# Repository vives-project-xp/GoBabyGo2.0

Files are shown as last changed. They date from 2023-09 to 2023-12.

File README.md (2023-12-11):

# GoBabyGo2.0

# Inhoudsopgave
1. [Inleiding](#inleiding)
2. [Nodige Onderdelen](#nodige-onderdelen)
3. [BOMlijst](#bomlijst)
4. [Rand Info](#rand-info)
5. [Digitale Joystick](#digitale-joystick)
6. [Analoge Joystick](#analoge-joystick)
7. [Motor Driver](#motor-driver)
8. [Potentiometer](#potentiometer)
9. [DC-DC Buck Converter](#dc-dc-buck-converter)
10. [Montage Ideeën](#montage-ideeën)
11. [PCB](#PCB)
12. [ESP32 Pinout](#esp32-pinout)

Alle info over het installeren van nodige programma's om te kunnen programmeren staat in het mapje [Programma's](./Programma's)

## inleiding
Ons doel is om kinderen met beperkte mobiliteit meer bewegingsvrijheid te geven. We vervangen het traditionele pedaal in auto's door een joystick die via een afstandsbediening kan worden bediend. De afstandsbediening heeft voorrang op de joystick. We hebben twee concepten voor de bevestiging van de joystick aan de auto: een dashboardmontage die de joystick van links naar rechts verplaatst, en een zijkantmontage die aan beide kanten kan worden geplaatst. Het brein van de auto is een ESP die de joystickinvoer leest en de motoren aanstuurt. Omdat de positie van de voorwielen niet kan worden ingelezen met de bestaande auto hardware, gebruiken we een potentiometer om dit probleem op te lossen.

## Nodige onderdelen

- Auto
- MicroController
- Motor driver voor te kunnen sturen
- Joystick
- DC-DC Converter

## BOMlijst
| **Onderdeel**            | **Prijs** | **Link**                                                                                                                                                                                                                                                                |
|--------------------------|-----------|-------------------------------------------------------------------------------------------------------------------------------------------------------------------------------------------------------------------------------------------------------------------------|
| **Motor Driver**         | €5.29     | https://www.amazon.com.be/-/en/OcioDual-Stepper-Electronics-Projects-Raspberry/dp/B07YNR5KWP/ref=sr_1_10?crid=13WDD3RB1V2TC&keywords=l298n+motor+driver&qid=1695624708&sprefix=l298n+motor+driver%2Caps%2C69&sr=8-10                                                    |
| **ESP32**                | €11.37    | https://www.amazon.com.be/-/en/ESP-32S-Development-Antenna-Bluetooth-Arduino/dp/B07XH45MWW/ref=sr_1_27?crid=2R7CSQ30VFE6H&keywords=esp32&qid=1695629494&sprefix=esp32%2Caps%2C166&sr=8-27&th=1                                                                          |
| **Joystick**             | €14.21    | https://www.amazon.com.be/-/en/Potentiometer-JH-D202X-R2-Controller-Photography-Accessories/dp/B09J2C4DN5/ref=sr_1_3?crid=357R56FNH75R6&keywords=Joystick+potentiometer+JH-D202X-R4+10K&qid=1695624613&sprefix=joystick+potentiometer+jh-d202x-r4+10k%2Caps%2C66&sr=8-3 |
| **DC-DC Buck Converter** | €11.88    | https://www.amazon.com.be/-/en/Hailege-Converter-1-25-36V-Adjustable-Step-down/dp/B07XRF9NWP/ref=sr_1_7?crid=1PQTSHA11MF1Q&keywords=dc+to+dc+buck+converter+adjustable&qid=1695628749&sprefix=dc+to+dc+buck+converter+adjustable%2Caps%2C71&sr=8-7                      |
| **Optocoupler** | €7.85    | https://www.amazon.com.be/-/en/BOJACK-Optocoupler-Installation-Spacing-Package/dp/B08CXKZ98W/ref=sr_1_6?crid=1FXUJNO9624LN&keywords=optocoupler&qid=1695634939&sprefix=optocoupler%2Caps%2C69&sr=8-6                      |
| **Connector PCB-Kabels** | €10.24    | https://www.amazon.com.be/-/en/Litorange-Female-2-54mm-JST-XH-Connector/dp/B086W9HB3M/ref=sr_1_1?crid=SXDRC5SCF07L&keywords=Picture+1+of+24+Click+to+enlarge+Have+one+to+sell%3F+Sell+it+yourself+Terminal+Board+Connectors+JST+Male+Female&qid=1695648512&s=home-improvement&sprefix=picture+1+of+24+click+to+enlarge+have+one+to+sell+sell+it+yourself+terminal+board+connectors+jst+male+female%2Chome-improvement%2C199&sr=1-1                      |
| **Connector kabels-kabels** | €13.99    | https://www.amazon.com.be/-/en/HSeaMall-Connector-Female-Housing-Assortment/dp/B0716WZ6RW/ref=sr_1_12?crid=3B4MFSYF52HO6&keywords=JST+conector+set&qid=1696247641&s=home-improvement&sprefix=jst+conector+set%2Chome-improvement%2C66&sr=1-12                     |
| **potentiometer** | €9.11    | https://www.amazon.com.be/-/en/Potentiometer-Rotating-Automotive-Electronics-Multimedia/dp/B09BJMFVMZ/ref=sr_1_11?crid=3GKNUFMRX9EJO&keywords=potentiometer+10k&qid=1696248212&s=home-improvement&sprefix=potentiometer+10k%2Chome-improvement%2C259&sr=1-11                      |

## Rand info

Batterij is 12v 

De huidige electronica komen de kabels met het volgende overeen:

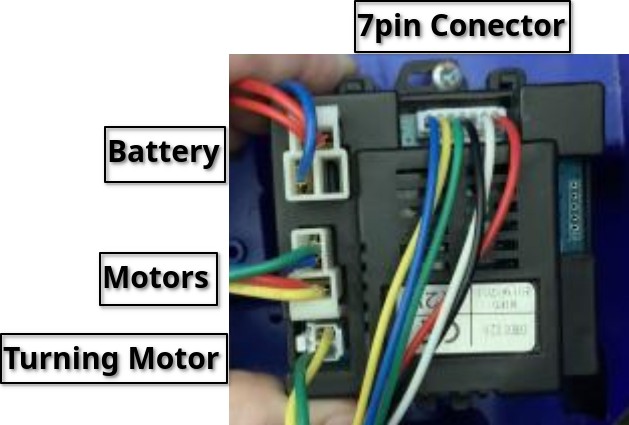
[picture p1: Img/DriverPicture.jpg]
Driver


De 7Pin Connector:
- Blauw: low high speed
- geel: vooruit
- Groen: achteruit
- zwart: grond
- empty
- wit: aanuitknop
- rood: aanuitknop

## Digitale Joystick
Om de auto te besturen zullen we een joystick gebruiken. De joystick die we in het begin tot onze beschikking hebben, is digitaal. 
In de toekomst overwegen we mogelijk over te schakelen naar een analoge joystick. Hoe je de joystick kunt binnenlezen kun je vinden onder het mapje [Programma's](./Programma's).

Zorg er voor dat de connector links onder zit dan klopt het schema.

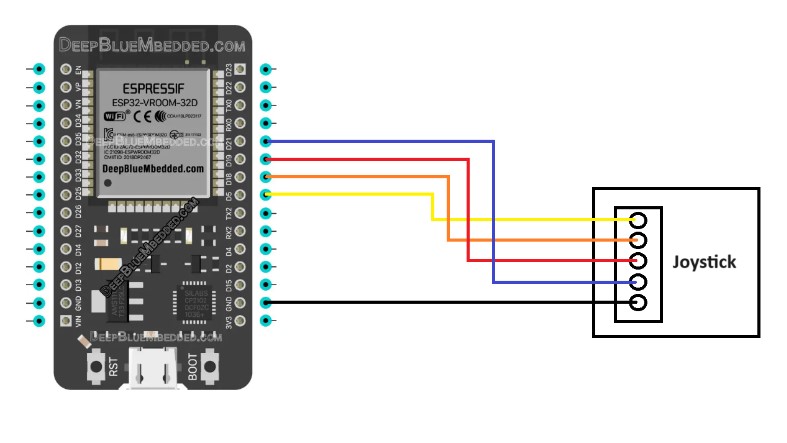
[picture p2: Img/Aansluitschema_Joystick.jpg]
Aansluitschema Joystick


## Analoge Joystick
Na het gebruik van een digitale joystick stappen we nu over naar een analoge variant voor het besturen van de auto. Een analoge
joystick maakt gebruik van variabele weerstand, waardoor we een vloeiendere en nauwkeurigere stuurinvoer kunnen realiseren. Ons
eindprogramma zal dan ook ontwikkeld worden met een analoge joystick. We hebben echter geen tussen programma's voor de analoge
joystick, omdat we deze al hebben gemaakt voor de digitale variant. Het zou overbodig zijn om dit proces opnieuw uit te voeren voor
de analoge joystick.

Een analoge joystick heeft twee potmeters. De beweging van de joystick zorgt voor variabele weerstand. Elke potmeter vertegenwoordigt
een richting: vooruit en achteruit (y-as) en links en rechts (x-as). Deze weerstanden worden omgezet in elektrische signalen, die
vervolgens worden gebruikt om de auto aan te sturen.

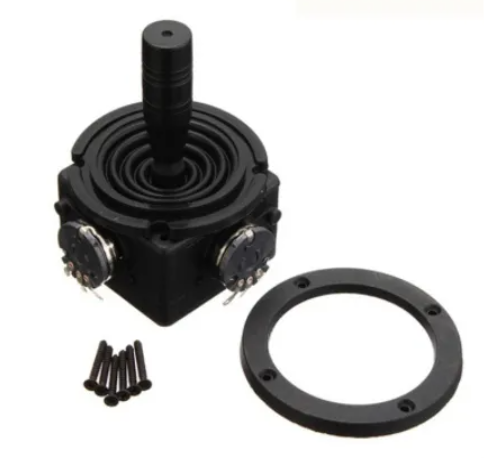
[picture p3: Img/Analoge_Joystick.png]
Analoge Joystick


## Motor driver
Om de richting te bepalen van de auto gebruiken we een motortje. Dit motortje wordt aangestuurd a.d.h.v een driver. 
Via deze driver kunnen we de richting en de snelheid van de motor bepalen. De driver die wij gebruiken is de L298N.
Hoe je de driver kunt gebruiken met een ESP kun je vinden in het mapje [Programma's](./Programma's).

De L298N is een motorcontroller-IC dat vaak wordt gebruikt in elektronische projecten. Het maakt gebruik van een H-brug-configuratie, waardoor het mogelijk is om
gelijkstroommotoren in beide richtingen aan te sturen. Met twee onafhankelijke kanalen is het geschikt voor het afzonderlijk aansturen van twee motoren, zoals bij
robotica wij gebruiker hier maar 1 van. Het ondersteunt een breed spanningsbereik en wordt gecontroleerd met logische signalen van bijvoorbeeld een microcontroller
zoals Arduino.

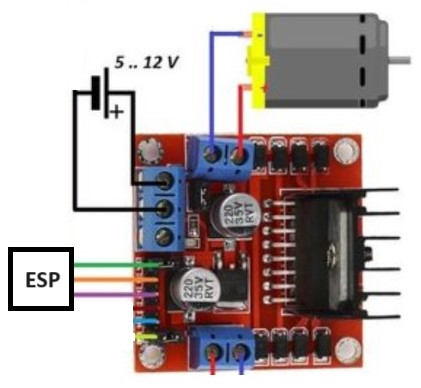
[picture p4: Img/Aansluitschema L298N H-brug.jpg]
Aansluitschema Driver
 

- Oranje,Paars: Richting motor
- Groen: Snelheid motor

## Potentiometer
Om de positie van onze wielen vast te stellen, maken we gebruik van een potentiometer. Een potentiometer, kortweg pot meter, is een elektronisch component dat wordt
ingezet om een variabele weerstand te creëren in een elektrisch circuit. In ons geval genereren we een analoog signaal op basis van deze weerstandswaarden, waarmee we
de positie van het stuur kunnen bepalen. Concreet wordt de potentiometer aan de stang bevestigd, die op zijn beurt is gekoppeld aan de wielen van de auto. Wanneer de
wielen van positie veranderen, wijzigt ook de positie van de potentiometer, waardoor we nauwkeurig de positie van de wielen kunnen achterhalen.

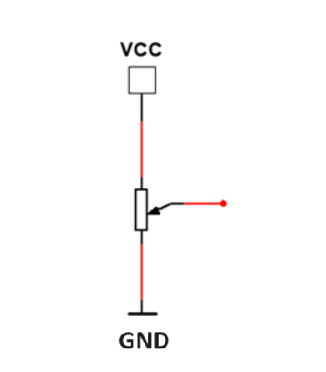
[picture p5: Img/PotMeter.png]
PotMeter


## DC-DC Buck Converter
Omdat niet al onze componenten op dezelfde spanning werken gebruiken we een Buck converter. Deze zorgt er voor dat we een hogere spanning
kunnen omzetten naar een lagere spanning. In de auto hebben we een baterij ter beschikking van 12 Volt maar onze esp heeft maar 5 volt nodig. 

Een DC-DC buck converter is een elektronisch apparaat dat de ingangsspanning van een gelijkstroombron verlaagt naar een lagere uitgangsspanning. Het werkt als een
efficiënte schakelende regelaar met behulp van componenten zoals transistors en een spoel (inductor). Deze converters worden veel gebruikt in elektronische apparaten om
de benodigde lagere spanning te leveren, zoals in batterijgevoede apparaten en voedingen voor microcontrollers.

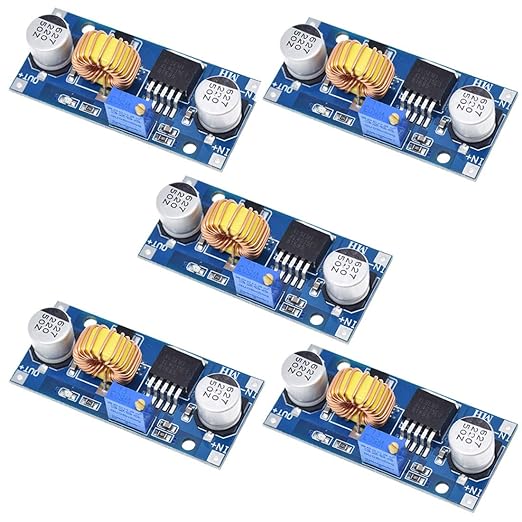
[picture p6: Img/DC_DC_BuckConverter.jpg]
BuckConverter


## montage ideeën
De joystick mag niet te veel ruimte innemen in de auto. Deze is geplaatst in een 3D-geprinte behuizing die aan een PVC-buis is bevestigd. We hebben voor een PVC-buis gekozen vanwege het lichte gewicht en de
mogelijkheid om de bekabeling erin te verbergen. We hebben twee concepten ontwikkeld voor het monteren van de joystick in de auto. Bij het eerste concept is de buis bevestigd aan het dashboard. Voor het tweede
concept wordt de buis aan de deur gemonteerd. In beide concepten kan de joystick links of rechts worden geplaatst, afhankelijk van de mobiliteit van het kind. We bevestigen de buizen met clips aan de auto.

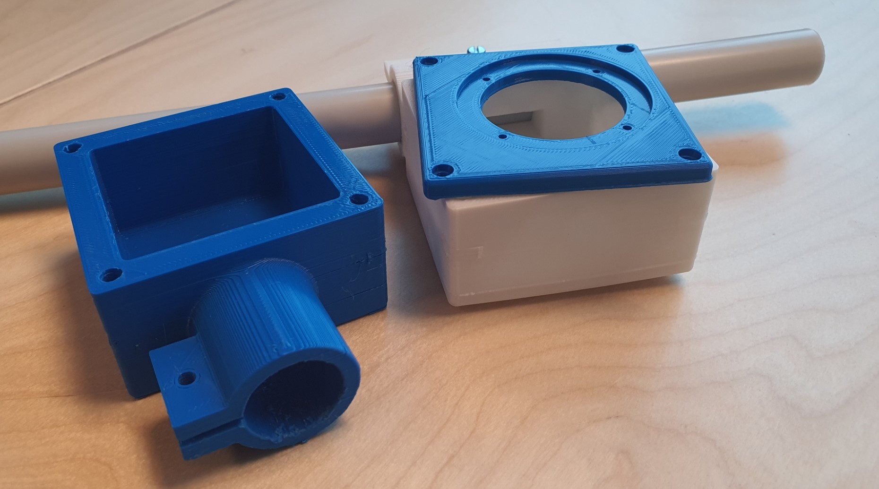
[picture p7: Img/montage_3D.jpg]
joystickbox


## PCB

### Inleiding

Meer info staat in de PCB directory.

### PCB layout

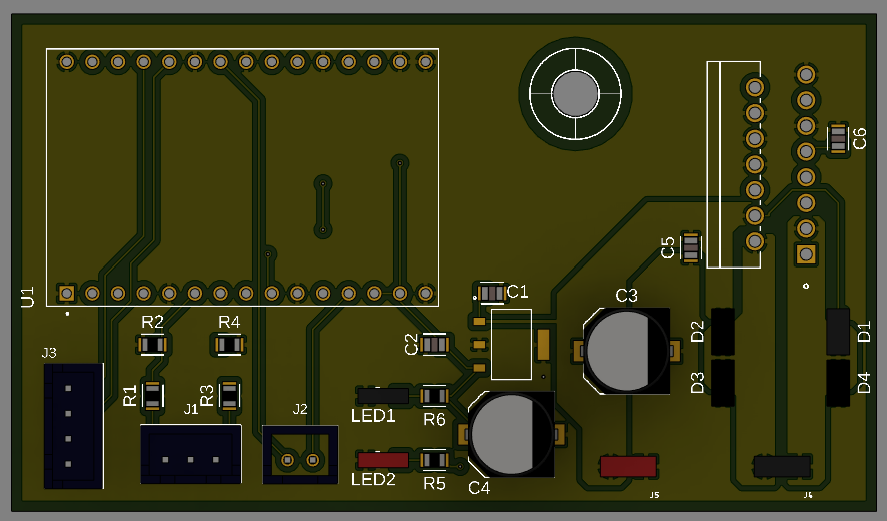
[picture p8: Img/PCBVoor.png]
PCBVoor


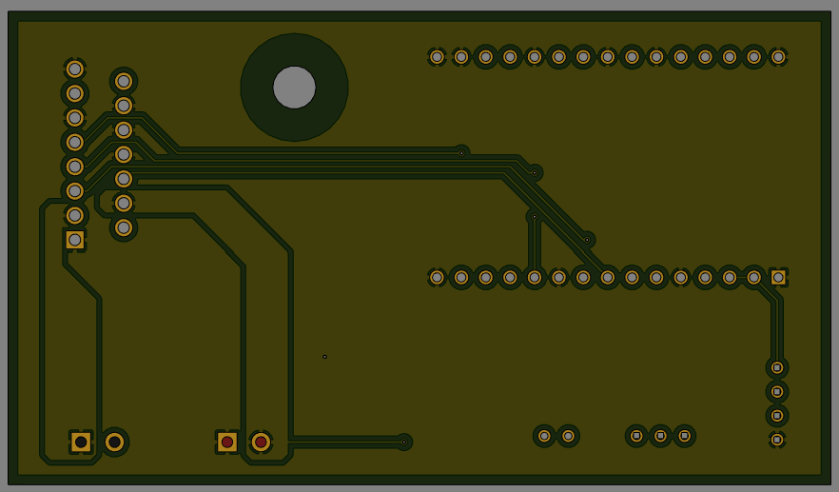
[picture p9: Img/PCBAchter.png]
PCBAchter


## ESP32 Pinout
- Driver
  - In1 = GPIO23
  - In2 = GPIO22
  - ENA = GPIO21
  - Channel = GPIO13

- Huidige elektronica
  - Forward = GPIO15
  - Backward = GPIO19
- Joystick
  - Xpin = GPIO2
  - Ypin = GPIO4

- Potentiometer
  - potPin = GPIO14

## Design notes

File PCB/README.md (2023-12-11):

# PCB

## inleiding

Ideal zouden we een PCB kunnen maken. Hier een korte aanzet om er aan te starten.

## Project files

De files zijn de archive en de .lbr.

## componenten

### Connectoren

Wel we hebben connectoren nodig.

- Connectoren set: https://www.amazon.com.be/-/en/YIXISI-Pieces-Connector-Connectors-Terminals/dp/B082ZLYRRN/ref=sr_1_1?crid=1NRPVG0VJ7JD6&keywords=Litorange%2B500%2Bx%2BJST%2BMale%2Band%2BFemale%2B2.54mm%2BJST-XH%2BJST%2BConnector%2Bwith%2BFemale%2BPin%2BConnector%2BWhite&qid=1701683827&s=home-improvement&sprefix=litorange%2B500%2Bx%2Bjst%2Bmale%2Band%2Bfemale%2B2.54mm%2Bjst-xh%2Bjst%2Bconnector%2Bwith%2Bfemale%2Bpin%2Bconnector%2Bwhite%2B%2Chome-improvement%2C73&sr=1-1&th=1
- Screw Terminals: https://be.farnell.com/multicomp-pro/mp011984/tb-wire-to-brd-r-a-2way-18awg/dp/4179014?st=screw%20terminals

### Gekozen componenten

De gebruikte componenten:
 - L298N : https://be.farnell.com/stmicroelectronics/l298n/ic-bridge-driver-dual-298/dp/403295?ICID=I-RP-STM7REC-1
 - ESP32 (->devkit<-) : https://www.mouser.be/ProductDetail/Espressif-Systems/ESP32-C3-DevKitC-02?qs=stqOd1AaK7%2F1Q62ysr4CMA%3D%3D
 - Voltage regulators : 
    -  5V: https://be.farnell.com/diodes-inc/az1117ch2-5-0trg1/ldo-dc-dc-conv-5v-0-8a-sot-223/dp/3942512
 - Diode: https://be.fa rnell.com/taiwan-semiconductor/es1dl-r3g/diode-ultra-fast-smf-1a-200v/dp/1559127
 - LEDs:
    - Green: https://be.farnell.com/multicomp-pro/mp008255/led-green-80mcd-576nm-1206/dp/3796283
    - Red: https://be.farnell.com/multicomp-pro/mp008281/led-red-100mcd-638nm-1206/dp/3796312
 - Weerstanden en condesatoren: Zie bomlijst.

 ### Reden keuze

Zie architectuur documenten om te zien wat we willen berijken. </br>

- L298N: Het is een veel gebruikte motordriver en simple te gebruiken.
- ESP32 Devkit: Dit hebben we liggen en het is dan gemakelijker om een pcb te maken. Moet geen rekening houden met de USB -> UART interface en we hebben dan geen 3.3V LDO meer nodig dan.
- Voltage regulator: we hebben 5V nodig voor de ESP en de MotorDriver te logica te voeden.

## Elektrisch schema

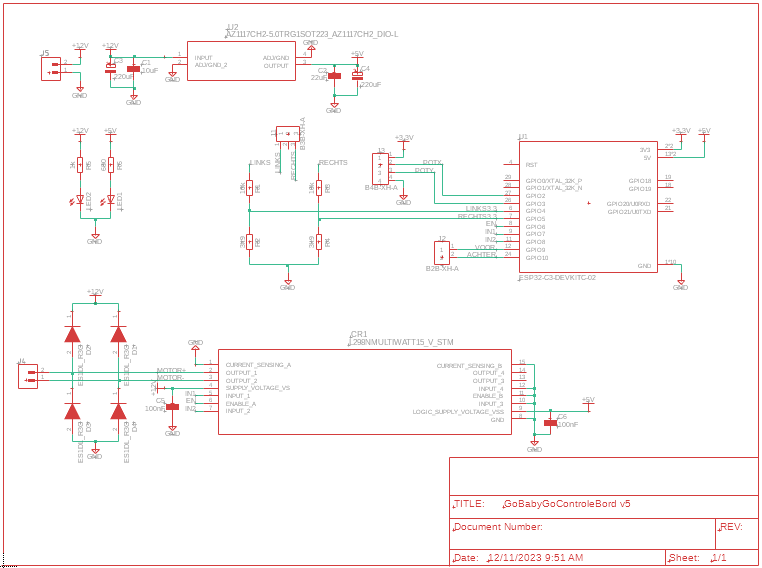
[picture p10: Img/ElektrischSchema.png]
Elektrisch schema


## PCB layout

PCBVoor

PCBAchter

## Bekabeling

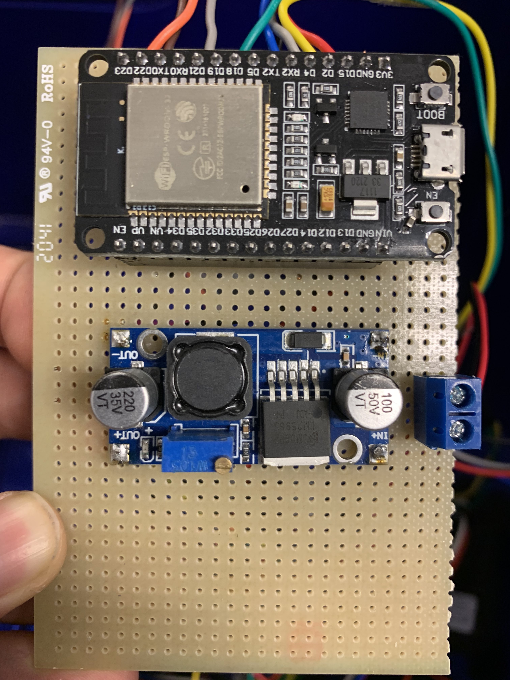
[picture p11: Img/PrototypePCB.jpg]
PrototypePCB


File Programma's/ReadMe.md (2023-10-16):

# Programma's

Om onze auto te laten rijden met behulp van een joystick, moeten we programmeren. Er zijn verschillende programma's om de verschillende delen van het project te testen. Deze programma's vormen allemaal bouwstenen die uiteindelijk het eindprogramma vormen.

## Voorbereiding 

Om te kunnen programmeren moeten we eerst verschillende programma's downloaden. Welke programma's je moet downloaden en hoe het werkt, kun je hieronder vinden.

### Arduino

Als je de verschillende tussenprogramma's wilt testen zul je arduino moeten downloaden. Dit kun je makkelijk downloaden via volgende
[Link](https://support.arduino.cc/hc/en-us/articles/360019833020-Download-and-install-Arduino-IDE "Arduino downloaden"). Arduino is een open-source elektronisch platform dat programmeerbaar is en gemakkelijk te gebruiken, zelfs voor beginners.

### Visual Studio Code

Ons eindprogramma wordt ontwikkeld in Visual Studio Code, een krachtige en veelzijdige code-editor die populair is vanwege zijn gebruiksvriendelijke interface en uitbreidbare functionaliteiten. Om deze code naar de ESP32 te uploaden, maken we gebruik van PlatformIO, een handige extensie voor Visual Studio Code die specifiek is ontworpen voor het bouwen en uploaden van code naar verschillende microcontrollerplatforms. Visual Studio Code is eenvoudig te downloaden en te gebruiken, en je kunt de nieuwste versie verkrijgen vanaf de officiële [website](https://code.visualstudio.com/download).

In Visual Studio Code moeten we nu PlatformIO downloaden. Als je links op "Extensions" klikt symbool met de vierkantjes, kun je zoeken naar PlatformIO en het vervolgens installeren.

| Opzoeken PlarformIO | PlarformIO installeren |
|--------------|--------------|
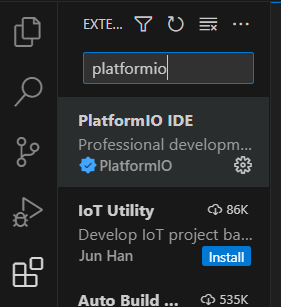
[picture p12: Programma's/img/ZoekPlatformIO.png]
Opzoeken PlarformIO
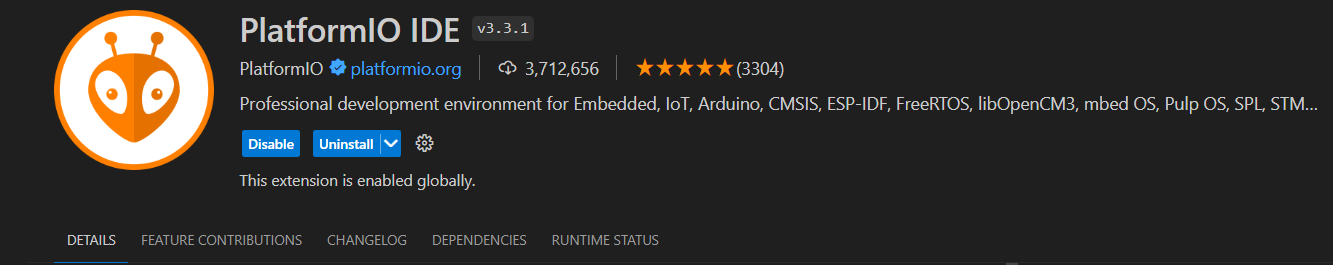
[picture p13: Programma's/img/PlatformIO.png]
PlarformIO installeren
|  ||

Om het eindprogramma te openen, ga je naar de map 'Eindprogramma' en open je Visual Studio Code via de terminal. Dit doe je door met de rechtermuisknop te klikken in de map 'Eindprogramma' en te kiezen voor 'Openen in terminal'. Zodra je in de terminal bent, typ je "code ." en druk je op Enter. Nu kun je het programma in Visual Studio Code uploaden naar je ESP32. De code zelf vind je in de 'src' map.

| Terminal openen | visual studio code openen |
|--------------|--------------|
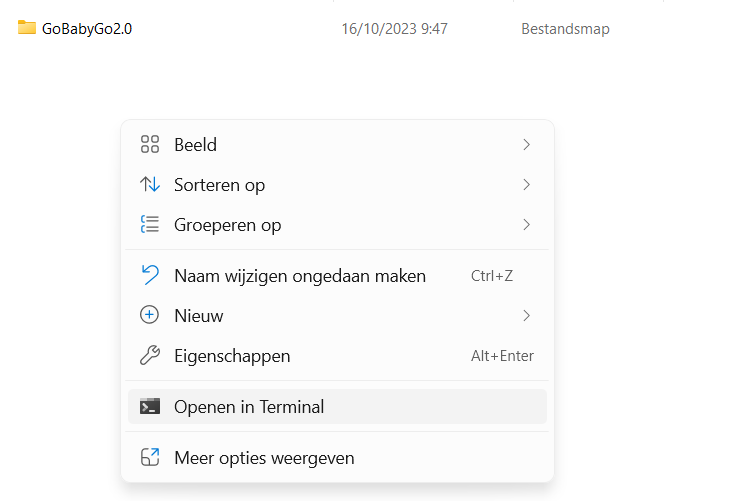
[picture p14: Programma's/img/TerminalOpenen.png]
Terminal openen
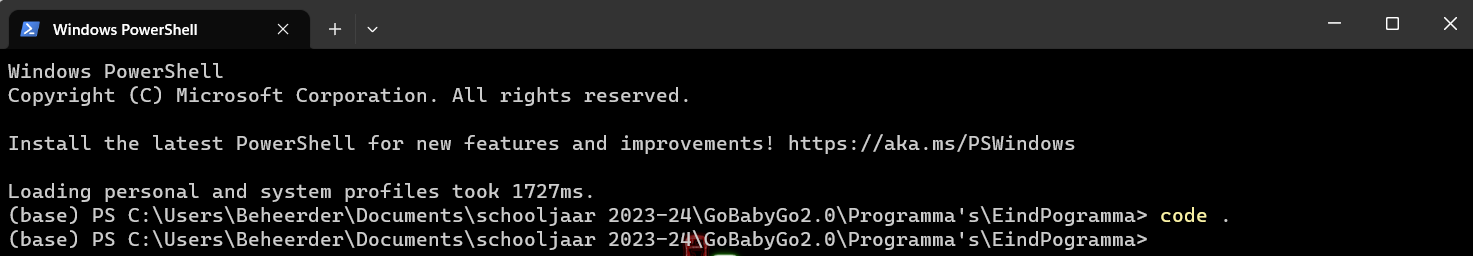
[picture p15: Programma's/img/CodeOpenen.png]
Code openen
|  ||

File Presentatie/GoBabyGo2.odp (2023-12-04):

## GoBabyGo2.0

Axel Brouckaert

Robbe De Wispelaere

Nikita Vandecasteele

## Analyse

- Stuur vervangen
- Joystick
- Bekabeling
- Programmeren
- Besturing ontwerp

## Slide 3

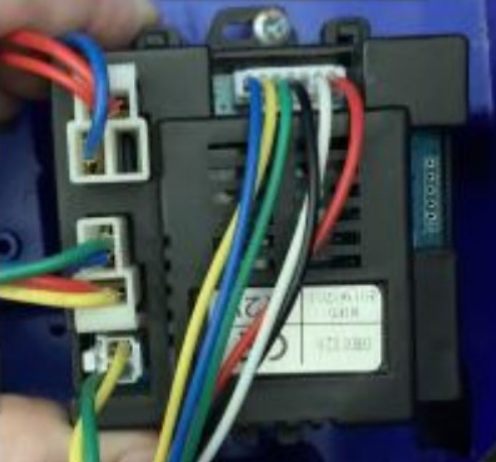
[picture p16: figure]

Onderzoek auto

- Welke elektronica zit er in?
- Bekabeling behouden?
- Eigen inbreng.

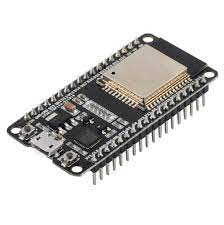
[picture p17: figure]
Amazon.com: DIYmall ESP32 DEVKIT ESP32-WROOM-32 Development Board ESP32 ESP-32S 2.4GHz WiFi+BT BLE Dual-core Dev Module CP2102 for Arduino DOIT : Electronics

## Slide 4

Bestaande besturing

De 7Pin Connector:

- Blauw: low high speed
- Geel: vooruit
- Groen: achteruit
- Zwart: grond
- Empty
- Wit: aanuitknop
- Rood: aanuitknop

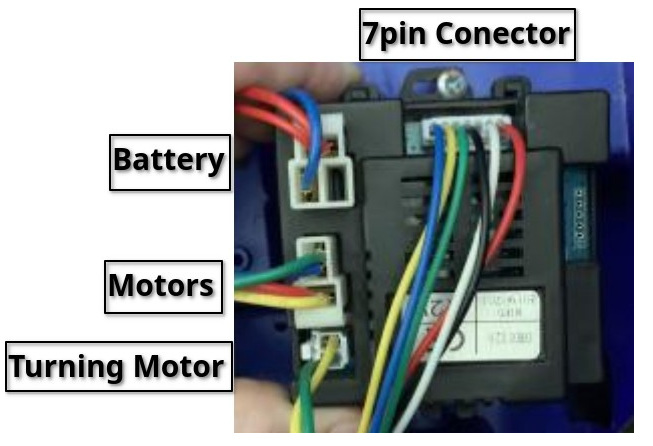
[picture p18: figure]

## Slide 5

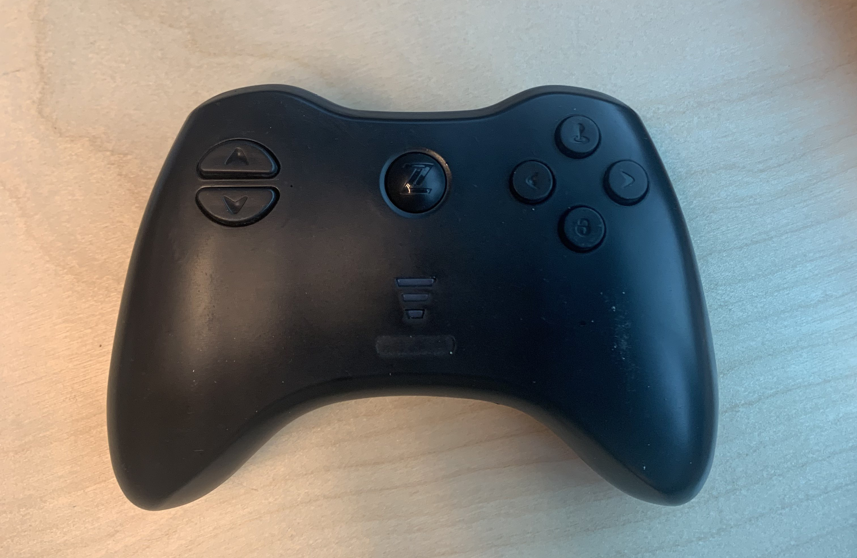
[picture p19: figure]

Nieuwe besturing

- Analoge of digitale Joystick?
- Wat met controller?

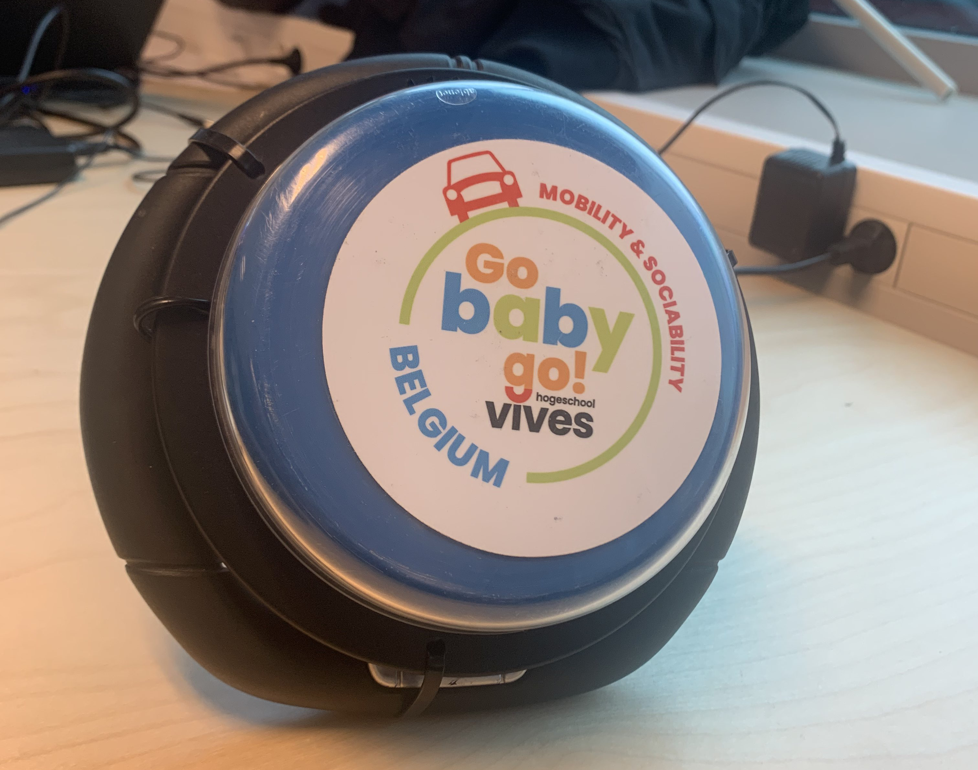
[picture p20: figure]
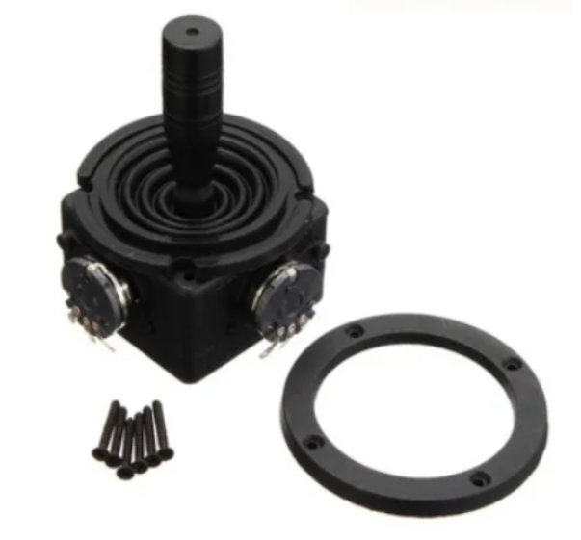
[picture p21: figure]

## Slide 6

Nieuwe Besturing

- Arduino
- Platform IO

Richting

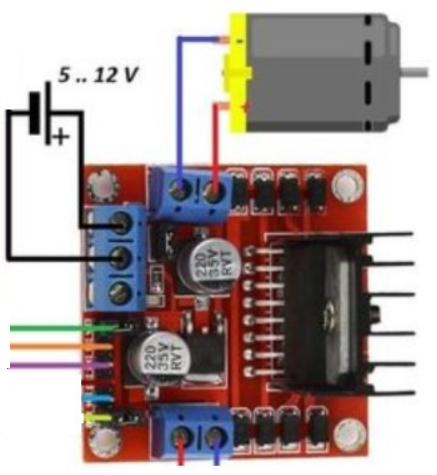
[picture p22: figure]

Snelheid V/A

Positie stuur

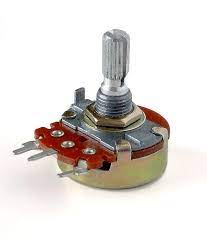
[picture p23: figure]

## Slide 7

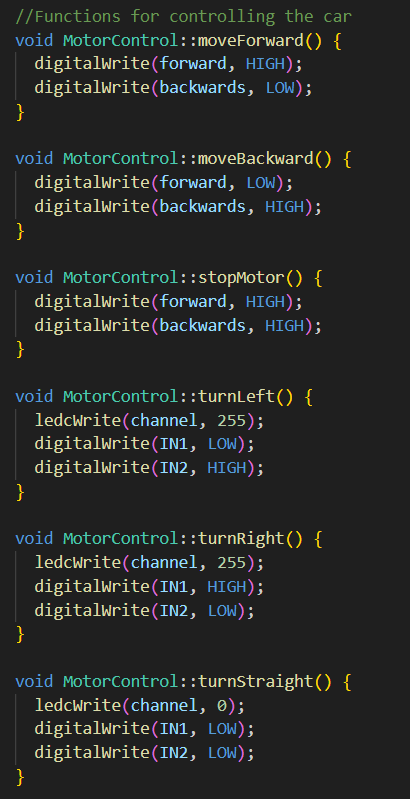
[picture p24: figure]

Praktische uitvoer

- Joystick binnen lezen
- Motor v/a aansturen
- Motor richting aansturen
- Potmeter binnen lezen
- Richting wielen bepalen

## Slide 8

Montage

- 2 concepten
- 3d prints
- Pvc buizen


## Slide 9

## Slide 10

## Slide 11

Niet afgewerkt

- Positie wielen bepalen.
- Automatisch positie van wielen naar midden.

Eindconclusie

Afgewerkt

- Joystick binnen lezen.
- Richting auto.
- Vooruit/Achteruit.
- Bekabeling in auto

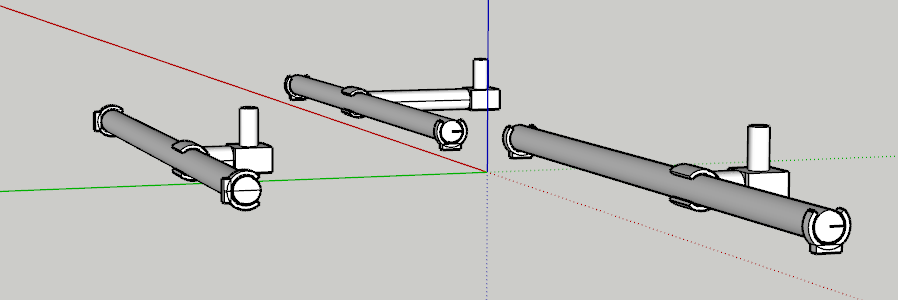
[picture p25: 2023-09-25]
Img/4schets3D.PNG

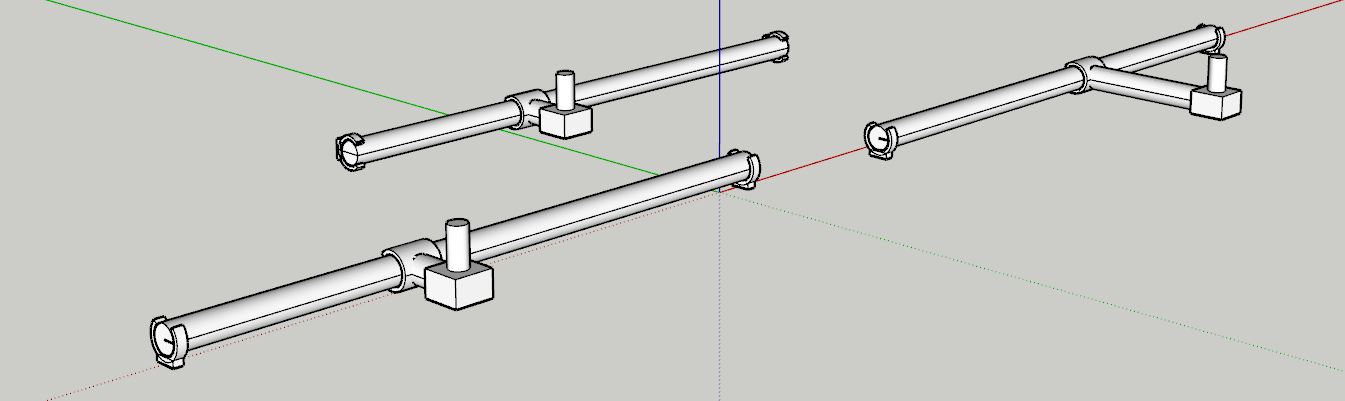
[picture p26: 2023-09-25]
Img/2schets3D.PNG

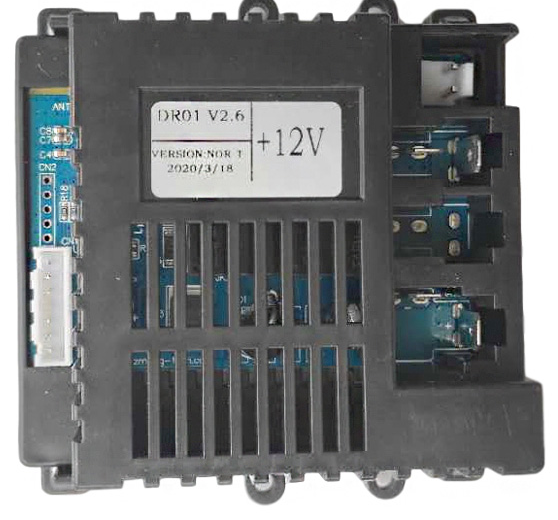
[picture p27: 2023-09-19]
Img/Driver.png

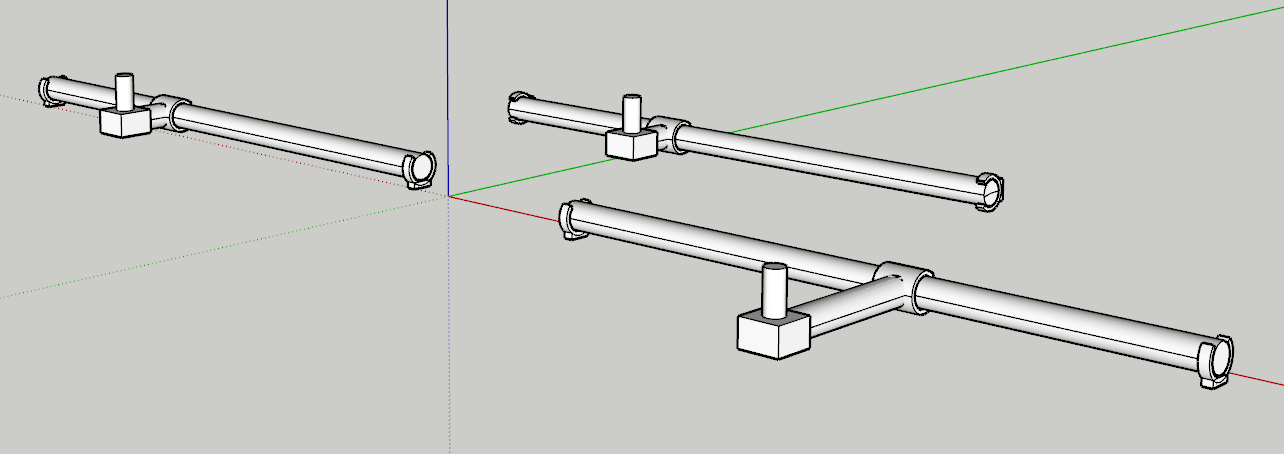
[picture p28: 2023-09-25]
Img/1schets3D.PNG

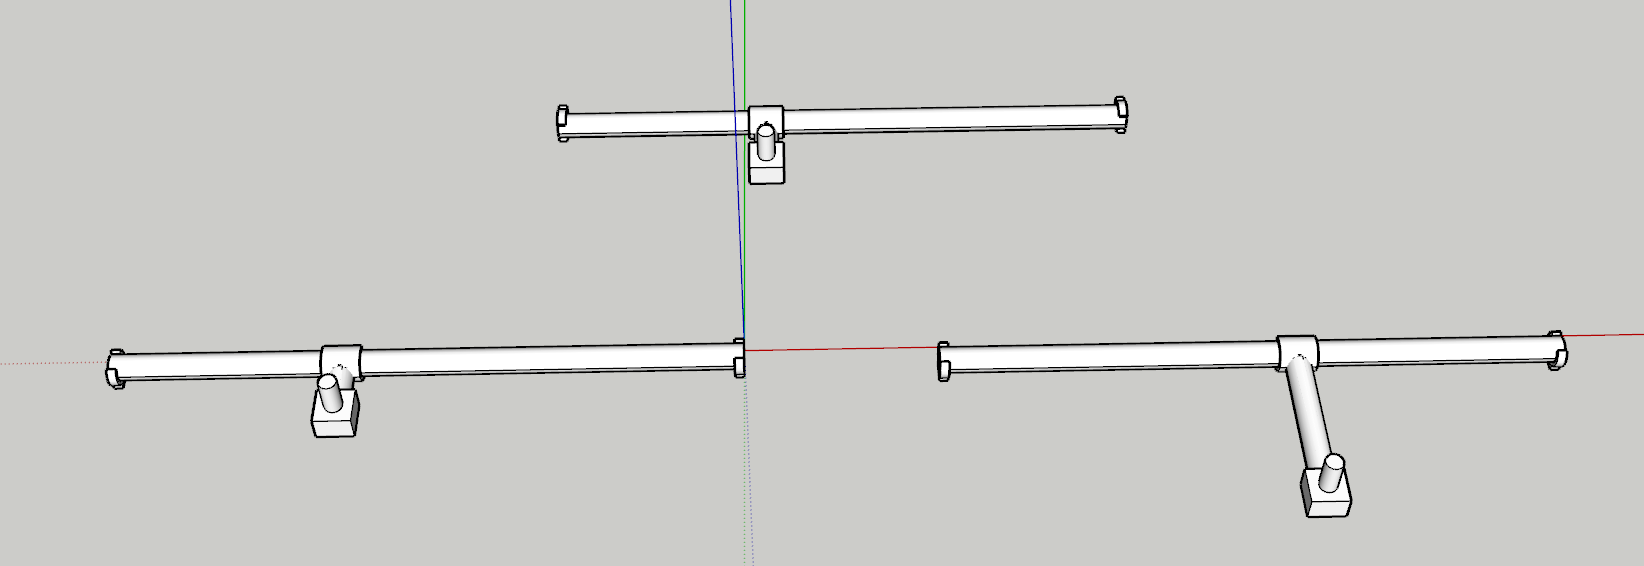
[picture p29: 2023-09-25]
Img/3schets3D.PNG

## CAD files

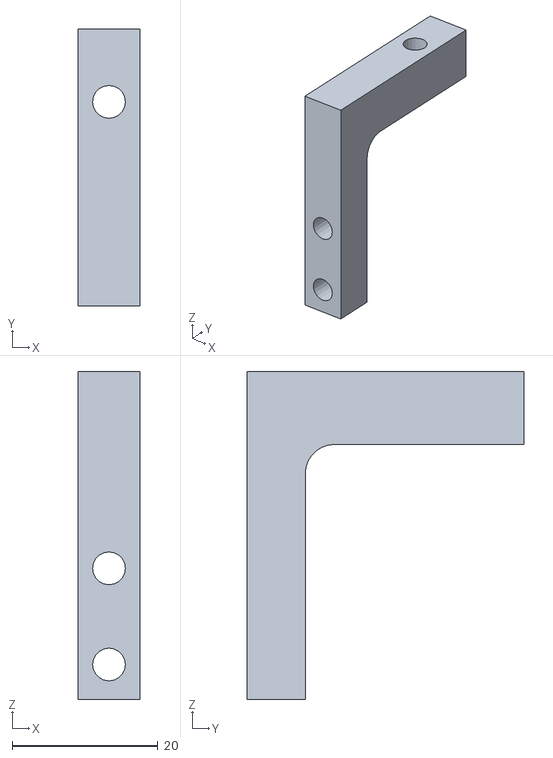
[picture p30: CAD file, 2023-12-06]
3Dtekeningen/stl_files/Lconector.stl
8.50 x 38.0 x 45.0

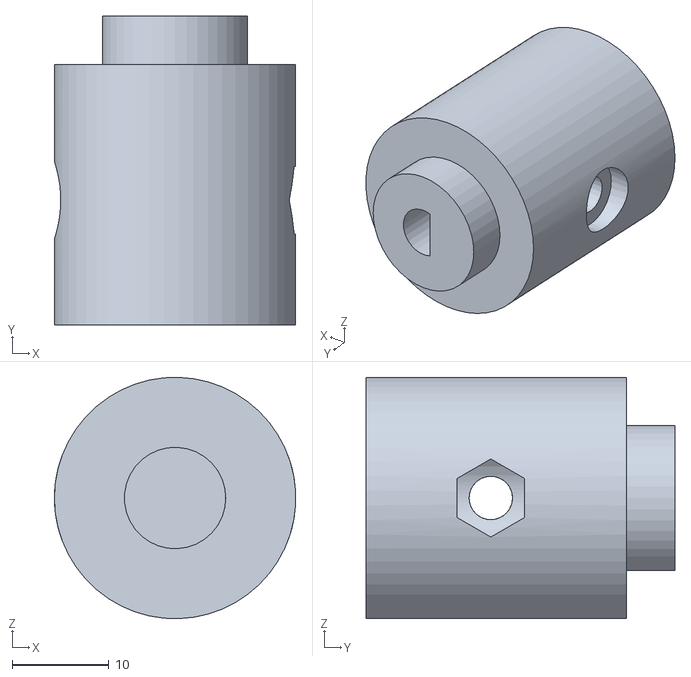
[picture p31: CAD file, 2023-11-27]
3Dtekeningen/stl_files/StuurPotentiometerConnector3.0.stl
25.0 x 32.0 x 25.0

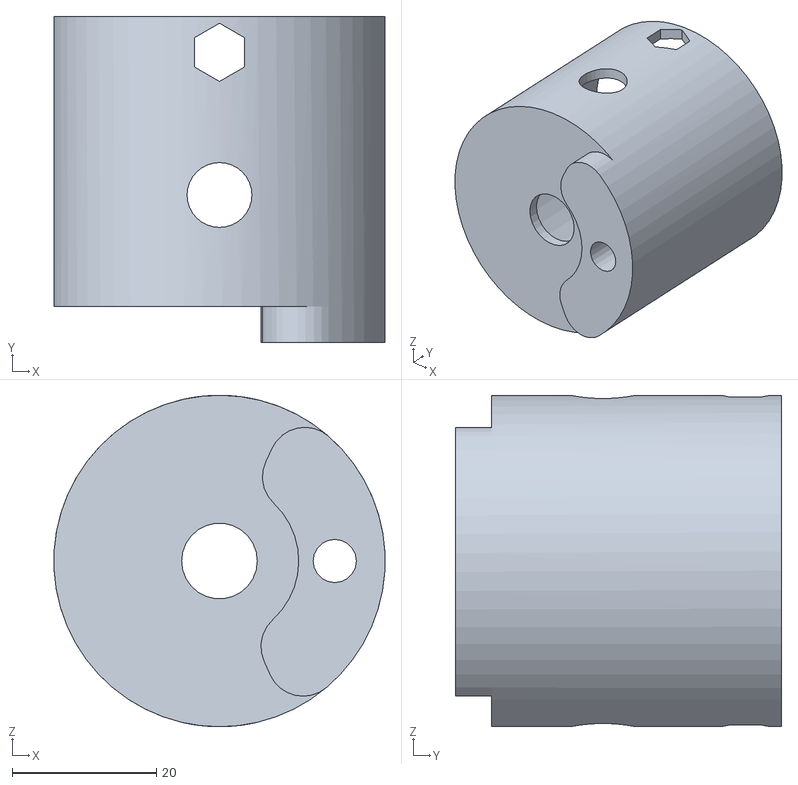
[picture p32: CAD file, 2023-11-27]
3Dtekeningen/stl_files/BasePotentiometer2.stl
45.9 x 45.3 x 46.0

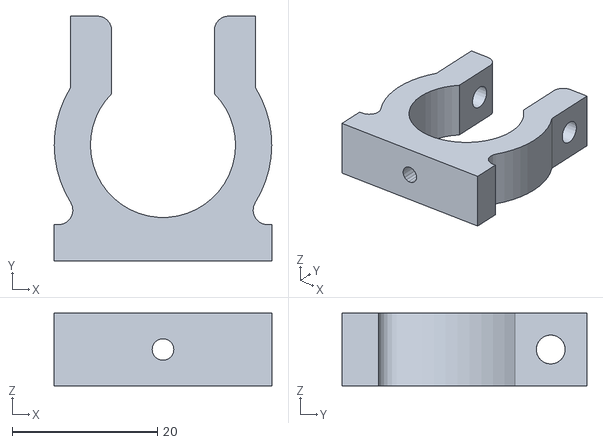
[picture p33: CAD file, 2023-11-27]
3Dtekeningen/stl_files/buisClip.stl
30.0 x 33.8 x 10.0

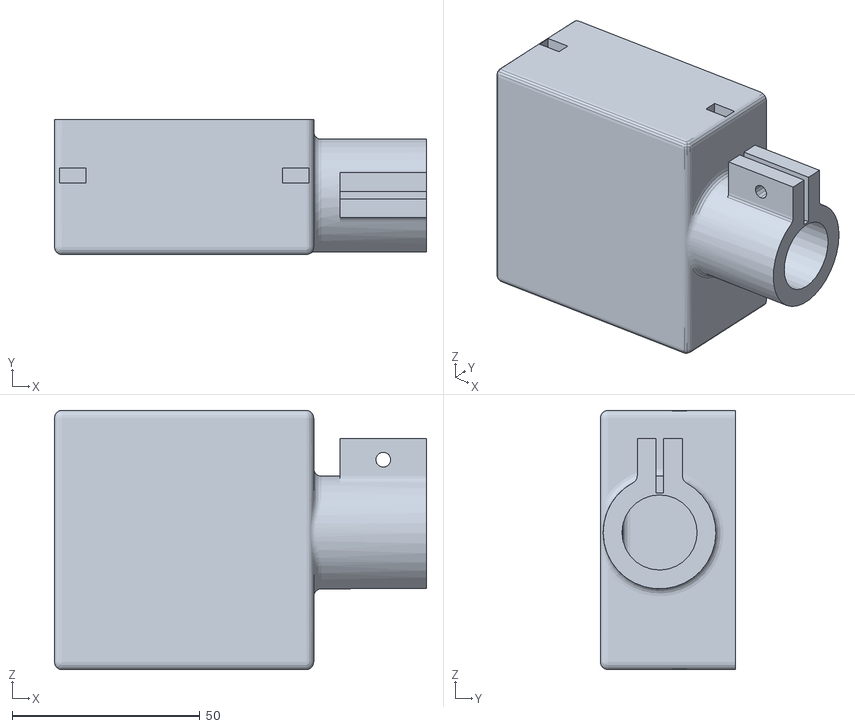
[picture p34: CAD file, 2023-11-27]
3Dtekeningen/stl_files/joystickBOX.stl
99.0 x 36.0 x 69.0

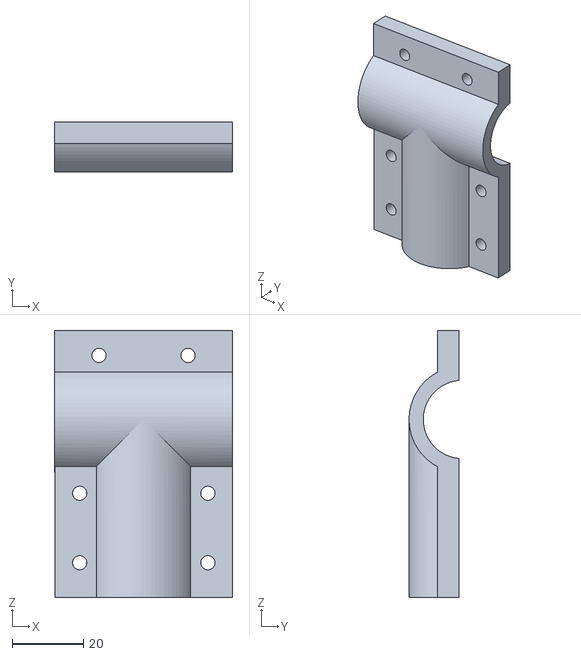
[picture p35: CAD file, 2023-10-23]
3Dtekeningen/stl_files/betterTconection.stl
50.0 x 14.0 x 75.0

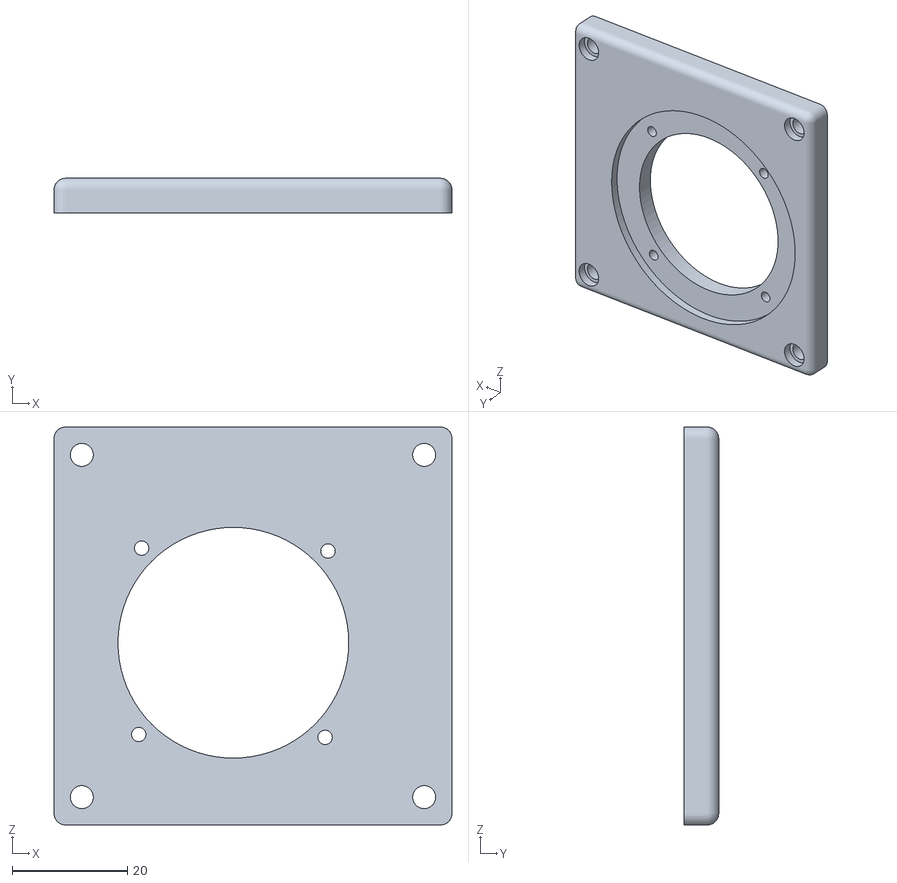
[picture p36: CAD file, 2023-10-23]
3Dtekeningen/stl_files/BETTERjoystickBOXtop.stl
69.0 x 6.00 x 69.0

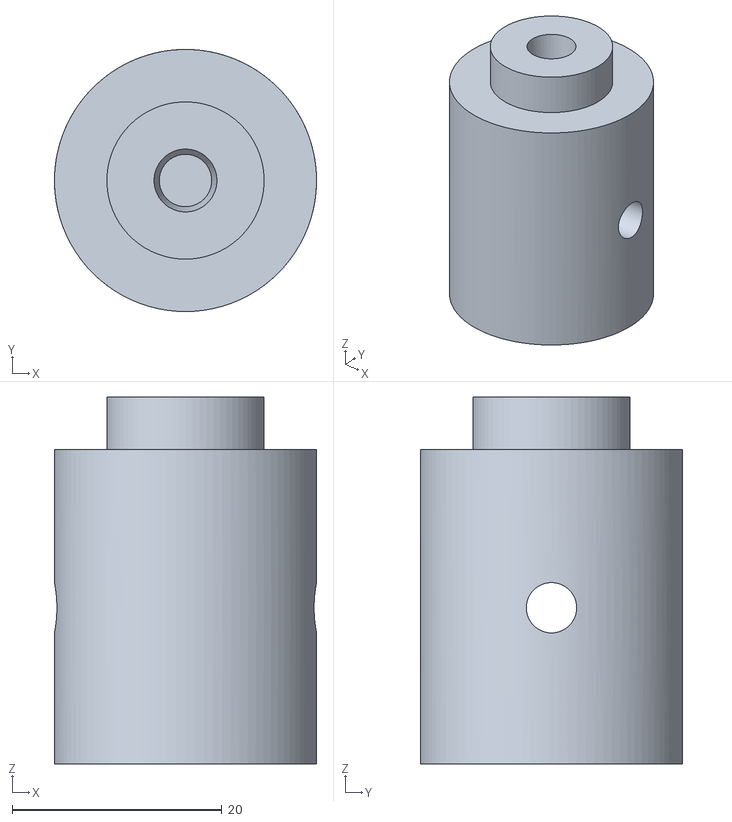
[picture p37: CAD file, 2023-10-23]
3Dtekeningen/stl_files/StuurPotentiometerConnector2.0.stl
25.0 x 25.0 x 35.0

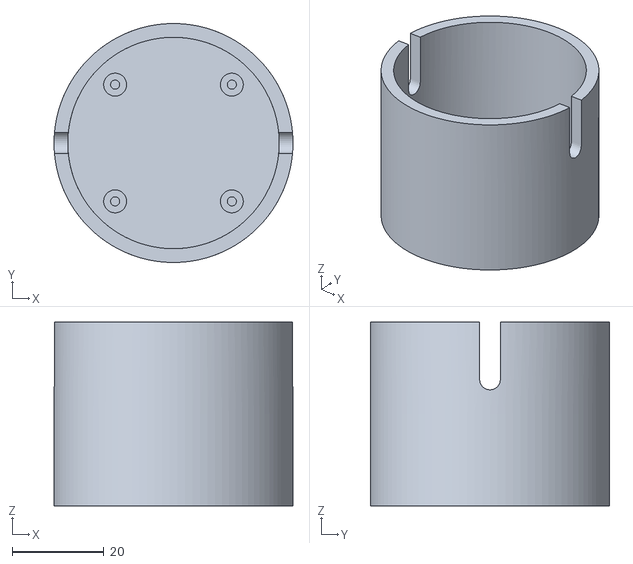
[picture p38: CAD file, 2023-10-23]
3Dtekeningen/stl_files/TopPotentiometer.stl
52.0 x 52.0 x 40.0

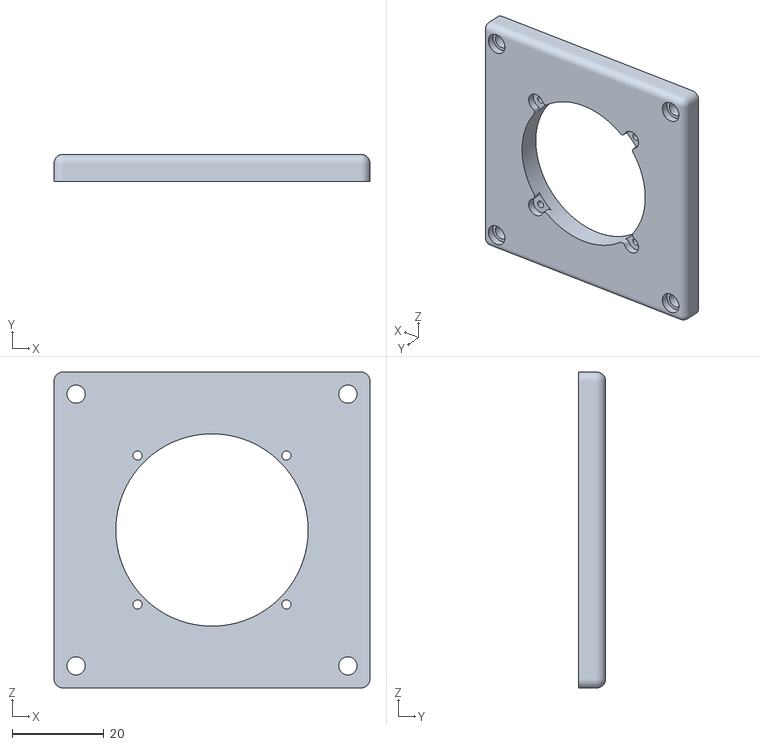
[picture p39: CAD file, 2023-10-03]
3Dtekeningen/stl_files/joystickBOXtop.stl
69.0 x 6.00 x 69.0

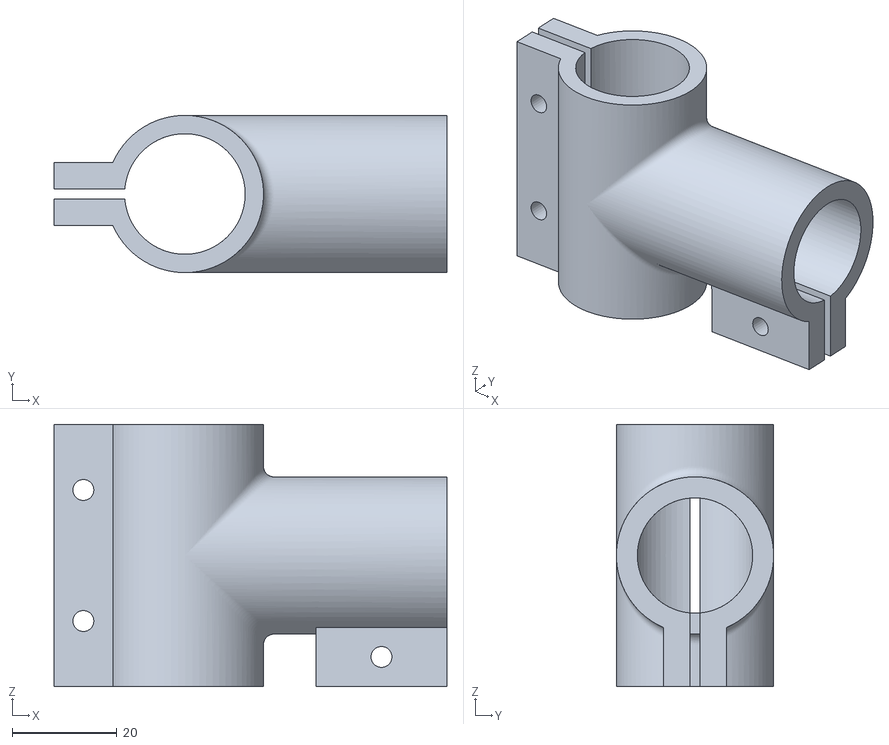
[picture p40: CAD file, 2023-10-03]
3Dtekeningen/stl_files/Tconection.stl
75.0 x 30.0 x 50.0

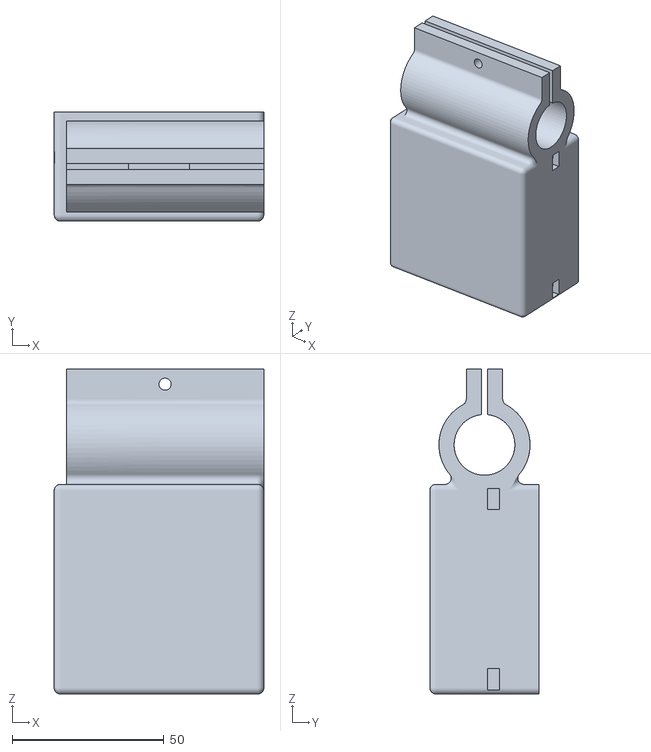
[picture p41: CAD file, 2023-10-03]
3Dtekeningen/stl_files/joystickBOXside.stl
69.0 x 36.0 x 107.0

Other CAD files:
3Dtekeningen/stl_files/BasePotentiometer.stl
3Dtekeningen/ipt_files/BasePotentiometer.ipt
3Dtekeningen/ipt_files/Lconector.ipt
3Dtekeningen/ipt_files/OldVersions/BasePotentiometer.0007.ipt
3Dtekeningen/ipt_files/OldVersions/StuurPotentiometerConnector2.0.0003.ipt
3Dtekeningen/ipt_files/OldVersions/Tconection.0003.ipt
3Dtekeningen/ipt_files/OldVersions/bevestigingpot.0001.ipt
3Dtekeningen/ipt_files/OldVersions/buisClip.0005.ipt
3Dtekeningen/ipt_files/OldVersions/joystickBOX.0006.ipt
3Dtekeningen/ipt_files/OldVersions/joystickBOXside.0006.ipt
3Dtekeningen/ipt_files/OldVersions/joystickBOXtop.0006.ipt
3Dtekeningen/ipt_files/StuurPotentiometerConnector.ipt
3Dtekeningen/ipt_files/StuurPotentiometerConnector2.0.ipt
3Dtekeningen/ipt_files/StuurPotentiometerConnector3.0.ipt
3Dtekeningen/ipt_files/Tconection.ipt
3Dtekeningen/ipt_files/TopPotentiometer.ipt
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

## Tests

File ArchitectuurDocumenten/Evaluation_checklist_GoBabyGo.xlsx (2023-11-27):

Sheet: Algemeen
 |  |  | T | Name: |  | T | Name: |  | T | Name:
 |  |  |  | Version: | Britbord Test |  | Version: | Gaatjesprint |  | Version: | Gaatjesprint
Test no | Test name | Subtest | 1 |  |  | 1 |  |  | 1
1 | Common
1.1 |  | Power Supply
2 | Control interfaces
2.1 |  | Joystick
2.2 |  | Motor Control | not done

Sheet: Testen Common
 |  |  |  |  |  | test 1
 |  |  | Wanted Values |  |  | Measured Value
1 | Common | Units | Minimal | Nominal | Maximum | Minimal | Nominal | Maximum
1.1 | Suply
1.2 | 12 | V | 11 | 12 | 14 |  | 12
1.3 | 5 | V | 4.9 | 5 | 5.1 |  | 5.02
1.4 | 3.3 | V | 3.2 | 3.3 | 3.4 |  | 3.26

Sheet: Testen Control Interfaces
 |  |  |  |  |  | Test 1 |  |  | Test 2 |  |  | Test 3
 |  |  | Wanted Values |  |  | Measured Value |  |  | Measured Value |  |  | Measured Value
1 | Control Interfaces | Units | Minimal | Nominal | Maximum | Minimal | Nominal | Maximum | Minimal | Nominal | Maximum | Minimal | Nominal | Maximum
1.1 | Joystick
1.1.1 | X-Waarde | V | 0.2 | 1.6 | 3.1 | 0.2 | 1.55 | 3.1 | 0.2 | 1.55 | 3.1 | 0.2 | 1.55 | 3.1
1.1.2 | Y-Waarde | V | 0.2 | 1.6 | 3.1 | 0.2 | 1.55 | 3.1 | 0.2 | 1.55 | 3.1 | 0.2 | 1.55 | 3.1
1.1.3 | PotWaarde | V | 0.5 | 1.6 | 3 | 0.2 | 1.55 | 3.1 | Deprecated |  |  | Deprecated
1.2 | Motor Control |  | Enabled | Disabled |  | If Enabled | If Disabled |  | If Enabled | If Disabled |  | If Enabled | If Disabled
1.2.1 | Vooruit | V | 3.3 | 0 |  | 3.2 | 0 |  | 3.2 | 0 |  | 3.2 | 0
1.2.2 | Achteruit | V | 3.3 | 0 |  | 3.2 | 0 |  | 3.2 | 0 |  | 3.2 | 0
1.2.3 | Links | V | 3.3 | 0 |  | 3.2 | 0 |  | 3.2 | 0 |  | 3.2 | 0
1.2.4 | Rechts | V | 3.3 | 0 |  | 3.2 | 0 |  | 3.2 | 0 |  | 3.2 | 0

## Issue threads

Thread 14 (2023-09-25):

### ISSUE TITLE
Motordriver aansturen.

### ISSUE THREAD

**Issue by Gibi500** [vives-project-xp/GoBabyGo2.0#14]

**Comment by RobbeDeW** [comment]
Aan de hand van de esp8266 willen we een motor laten draaien a.d.h.v een driver(L298N)

**Comment by RobbeDeW** [comment]
Info van de driver in de ReadMe gezet.

**Comment by RobbeDeW** [comment]
Nog kleine aanpassingen gedaan aan het aansluitschema van de driver.

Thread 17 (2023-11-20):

### ISSUE TITLE
Aandrijving aansturen

### ISSUE THREAD

**Issue by Gibi500** [vives-project-xp/GoBabyGo2.0#17]

**Comment by RobbeDeW** [comment]
We laten de auto vooruit en achteruit rijden a.d.h.v een joystick. Dit wordt gedaan met een ESP8266 we zullen dan later nog overschakelen naar een ESP32.

**Comment by RobbeDeW** [comment]
Aangezien het deel van de potmeter niet meer wordt uitgevoerd worden zijn we hier klaar mee

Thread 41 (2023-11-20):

### ISSUE TITLE
Wielen regelen zodat ze standaard rechtdoor staan.

### ISSUE THREAD

**Issue by Gibi500** [vives-project-xp/GoBabyGo2.0#41]
Probleem: De wielen kunnen standaard op een hoek staan door tolerantie van de auto.

Is het mogelijk om op te lossen in software of hardware of iets anders...

**Comment by Gibi500** [comment]
We kunnen een trim potentiometer in serie zetten met de potentiometer van de stuur. Er kan dan gewoon in software de waarde waar de stuur wilt gaan  voor centerpositie aan passen aan de nieuwe schakeling.

Het kan dat dit niet werkt doordat de wielen te los staan waardoor de wielen nooit "recht" kunnen staan.

Maar we kunnen dat pas maar uittesten als we het proberen...

**Comment by RobbeDeW** [comment]
Vanwege de beperkte beweging van de wielenstang kunnen we deze niet nauwkeurig meten met een potentiometer. Na overleg met de leerkrachten hebben we gezocht naar alternatieve oplossingen. Helaas zijn we gezamenlijk tot de conclusie gekomen dat het met de beschikbare tijd niet haalbaar is om dit aspect van ons project te realiseren. Daarom hebben we besloten om dit deel van ons project te laten vervallen.

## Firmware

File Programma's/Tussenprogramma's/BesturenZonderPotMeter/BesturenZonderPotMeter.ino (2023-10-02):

//driver
const int IN1 = 23;
const int IN2 = 22;
const int ENA = 4;
// Kies een PWM-kanaal (0-15) dat beschikbaar is voor je board
const int channel = 13;

//Input pinnen joystick
int rightpin = 18;
int leftpin = 5;
int uppin = 19;
int downpin = 21;

//output pinnen motor V/A
int forward = 15;
int backwards = 2;

//Status joystick
int leftvalue = 0;
int rightvalue = 0;
int upvalue = 0;
int downvalue = 0;

void setup() {
  pinMode (IN1, OUTPUT);
  pinMode (IN2, OUTPUT);
  ledcSetup(channel, 5000, 8);// Kanaal, frequentie (Hz), resolutie (bits)
  ledcAttachPin(ENA, channel);

  pinMode(forward,OUTPUT);
  pinMode(backwards,OUTPUT);
  
  pinMode(leftpin,INPUT_PULLUP);
  pinMode(rightpin,INPUT_PULLUP);
  pinMode(uppin,INPUT_PULLUP);
  pinMode(downpin,INPUT_PULLUP);
  Serial.begin(9600);
}

void loop() {
  leftvalue= digitalRead(leftpin);
  rightvalue= digitalRead(rightpin);
  upvalue= digitalRead(uppin);
  downvalue= digitalRead(downpin);

  //Vooruit
  if(upvalue == 0){
    Serial.println("Voorruit");
    digitalWrite(forward,HIGH);
    digitalWrite(backwards,LOW);
    //Schuinvooruit
    if(leftvalue==0){
      digitalWrite(forward,HIGH);
      digitalWrite(backwards,LOW);
      
      ledcWrite(channel, 255);
      digitalWrite(IN1, LOW);
      digitalWrite(IN2, HIGH);
      Serial.println("Shuinlinks Vooruit");
    }
    if(rightvalue==0){
      digitalWrite(forward,HIGH);
      digitalWrite(backwards,LOW);
      
      ledcWrite(channel, 255);
      digitalWrite(IN1, HIGH);
      digitalWrite(IN2, LOW);
      Serial.println("schuinrechts Vooruit");
    }
  }
  
  //Achteruit
  else if(downvalue== 0){
    Serial.println("Acheruit");
    digitalWrite(forward,LOW);
    digitalWrite(backwards,HIGH);
    //Schuinachteruit
    if(leftvalue==0){
      digitalWrite(forward,LOW);
      digitalWrite(backwards,HIGH);
      
      ledcWrite(channel, 255);
      digitalWrite(IN1, LOW);
      digitalWrite(IN2, HIGH);
      Serial.println("Shuinlinks achteruit");
    }
    if(rightvalue==0){
      digitalWrite(forward,LOW);
      digitalWrite(backwards,HIGH);
      
      ledcWrite(channel, 255);
      digitalWrite(IN1, HIGH);
      digitalWrite(IN2, LOW);
      Serial.println("schuinrechts achteruit");
    }
  }
  
  else{
    Serial.println("Auto staat stil");
    digitalWrite(forward,LOW);
    digitalWrite(backwards,LOW);
  }
}

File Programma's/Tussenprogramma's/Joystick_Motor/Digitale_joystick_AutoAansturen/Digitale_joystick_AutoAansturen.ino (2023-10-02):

//Input pinnen joystick
int leftpin = 14;
int rightpin = 12;
int uppin = 13;
int downpin = 4;

//output pinnen motor V/A
int forward = 0;
int backwards = 2;

//Status joystick
int leftvalue = 0;
int rightvalue = 0;
int upvalue = 0;
int downvalue = 0;

void setup() {
  pinMode(leftpin,INPUT_PULLUP);
  pinMode(rightpin,INPUT_PULLUP);
  pinMode(uppin,INPUT_PULLUP);
  pinMode(downpin,INPUT_PULLUP);
  pinMode(forward,OUTPUT);
  pinMode(backwards,OUTPUT);
  Serial.begin(9600);
}

void loop() {
  leftvalue= digitalRead(leftpin);
  rightvalue= digitalRead(rightpin);
  upvalue= digitalRead(uppin);
  downvalue= digitalRead(downpin);

  if(upvalue == 0){
    Serial.println("Auto gaat voorruit");
    digitalWrite(forward,HIGH);
    digitalWrite(backwards,LOW);
  }
  else if(downvalue== 0){
    Serial.println("Auto gaat acheruit");
    digitalWrite(forward,LOW);
    digitalWrite(backwards,HIGH);
  }
  else{
    Serial.println("Auto staat stil");
    digitalWrite(forward,LOW);
    digitalWrite(backwards,LOW);
  }

}

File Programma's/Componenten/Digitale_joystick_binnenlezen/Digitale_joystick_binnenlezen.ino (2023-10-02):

int leftpin = 18;
int rightpin = 5;
int uppin = 19;
int downpin = 21;

int leftvalue = 0;
int rightvalue = 0;
int upvalue = 0;
int downvalue = 0;

void setup() {
  pinMode(leftpin,INPUT_PULLUP);
  pinMode(rightpin,INPUT_PULLUP);
  pinMode(uppin,INPUT_PULLUP);
  pinMode(downpin,INPUT_PULLUP);
  Serial.begin(9600);
}

void loop() {
  leftvalue= digitalRead(leftpin);
  rightvalue= digitalRead(rightpin);
  upvalue= digitalRead(uppin);
  downvalue= digitalRead(downpin);
  
  Serial.print(leftvalue);
  Serial.print(" left ");
  Serial.print(rightvalue);
  Serial.print(" right ");
  Serial.print(upvalue);
  Serial.print(" up ");
  Serial.print(downvalue);
  Serial.print(" down ");
  Serial.println();
  delay(500);
}

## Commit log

2023-09-18 Heb folders gemaakt voor de concepten en schetsen.
2023-09-25 3d concept schets
    [schets3Dconcept.skp]
2023-09-25 Connectors toegevoegd aan de bestellijst
2023-09-26 verder gewerkt aan de 3d tekening
    [Tconection.0001.ipt, Tconection.ipt, buisClip.0001.ipt, buisClip.ipt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]
2023-10-02 gewerkt aan de 3d prints en concept affiche
    [Tconection.0001.ipt, Tconection.0002.ipt, Tconection.ipt, buisClip.0001.ipt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]
2023-10-03 stl files
    [Tconection.stl, buisClip.stl, joystickBOX.0004.ipt, joystickBOX.0005.ipt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]
2023-10-16 Porogramma toegevoegd aan de hand van PlatformIo
2023-10-23 3d tekeningen voor pot meter
    [BasePotentiometer.ipt, BasePotentiometer.stl, StuurPotentiometerConnector.ipt, StuurPotentiometerConnector2.0.ipt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]
2023-10-23 3d tekeningen bijgewerkt
    [BETTERjoystickBOXtop.stl, betterTconection.ipt, betterTconection.stl, joystickBOXtop.0004.ipt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]
2023-11-06 de 3dtekeningen van de potmeter bijgewerkt
    [BasePotentiometer.0005.ipt, BasePotentiometer.ipt, StuurPotentiometerConnector2.0.0003.ipt, StuurPotentiometerConnector2.0.ipt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]
2023-11-06 stl en ipt files alk een aparte map gegeven
    [BETTERjoystickBOXtop.stl, BasePotentiometer.0005.ipt, BasePotentiometer.ipt, BasePotentiometer.stl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]
2023-11-20 dingen in commentaar gezet die we niet nodig hebben
2023-11-27 Added Docs
    [Evaluation_checklist_GoBabyGo.xlsx]
2023-11-27 stl file
    [StuurPotentiometerConnector3.0.stl]
2023-11-27 def interfaces
    [Definitie_Inerfaces.xlsx]
2023-12-04 Added start PCB design
2023-12-04 L conector
    [Lconector.ipt, Lconector.stl]
2023-12-06 PCB gemaakt
2023-12-11 update the PCB files
2023-12-13 fixed PCB
